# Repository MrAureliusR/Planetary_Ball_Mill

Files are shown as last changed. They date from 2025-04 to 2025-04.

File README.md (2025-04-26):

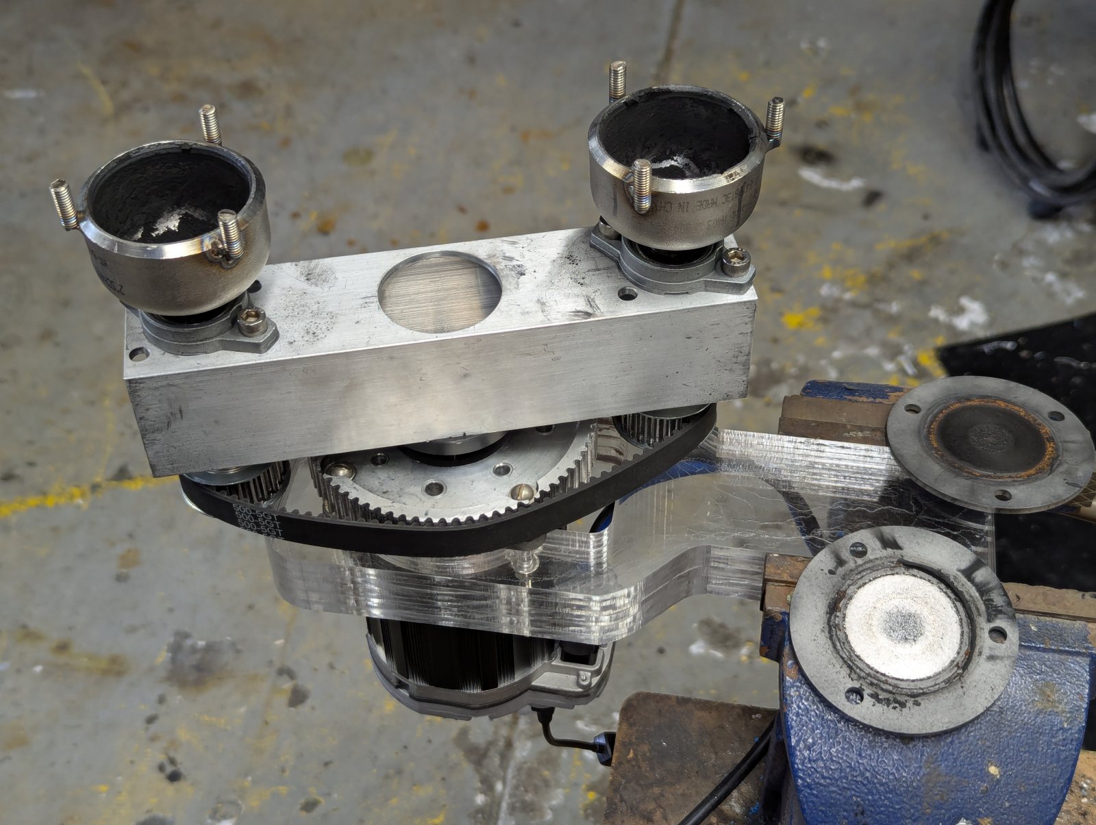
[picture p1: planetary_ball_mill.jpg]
Planetary ball mill photo Planetary Ball Mill
<br>
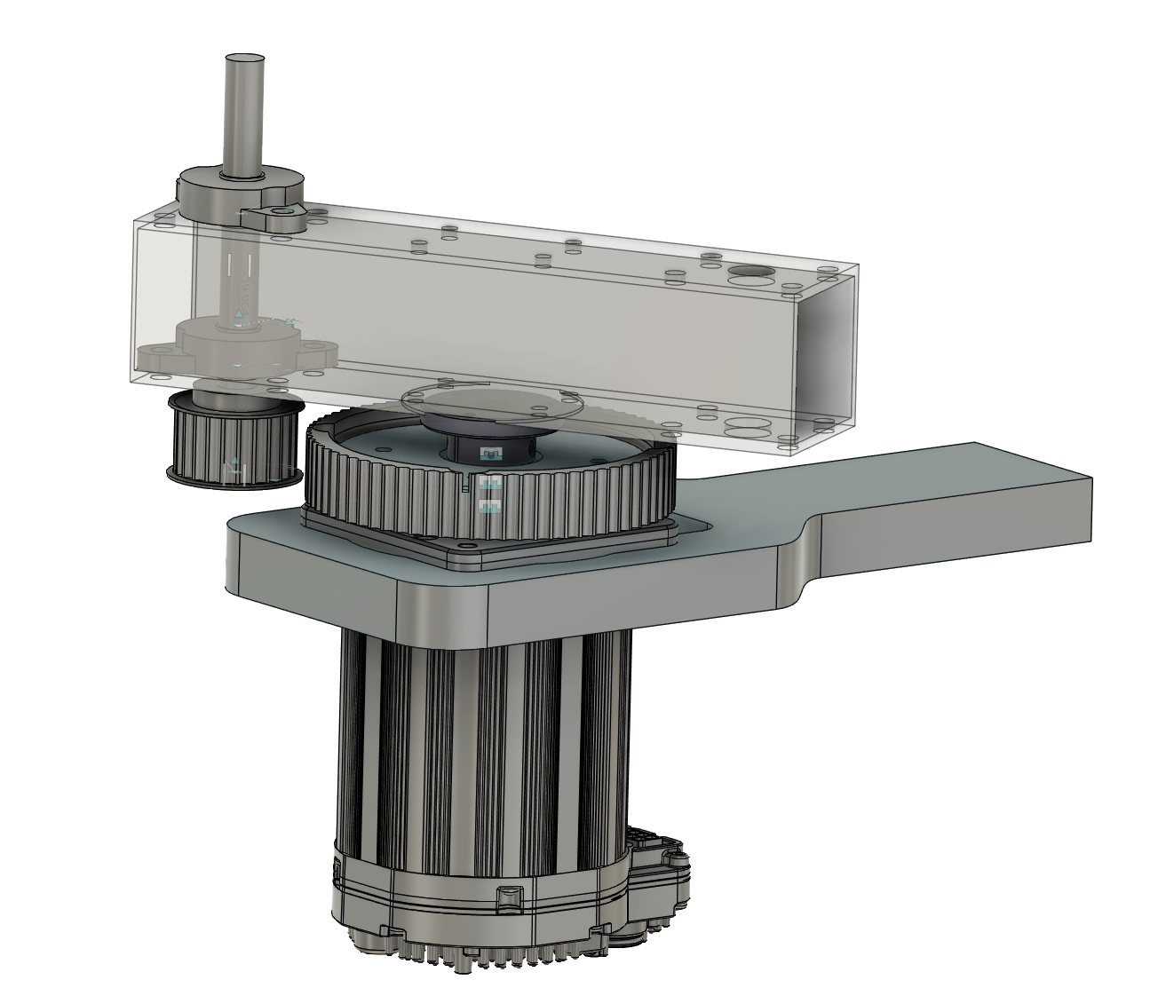
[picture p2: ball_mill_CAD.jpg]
Planetary ball mill CAD Planetary Ball Mill CAD


Modeled after this commercial device:  https://www.retsch.com/products/milling/ball-mills/planetary-ball-mill-pm-100/<br>
<br><br>
Chambers counter-rotate 2X speed of motor<br>
Chamber path radius: 85mm<br>
Chamber diameter: 50mm<br>
Chamber height: 30mm<br>
Chamber volume:  60ml (appx)<br>
<br><br>
Radius to chamber outer wall (85 + 25 =  110mm)
<br>
g-force at 600RPM:  44g
<br>
Power consumption:<br>
Idle: 16W<br>
600RPM chambers empty: 45W<br>
600RPM 15 9.5mm balls in each chamber:  110W<br>
600RPM 96 6.35mm balls in each chamber:  200W<br>
<br><br><br>

Rectangular aluminum tube (main beam):  https://www.mcmaster.com/6546K23/  $25<br>
Sun pulley:  https://phidgets.com/?prodid=779   GT5 Pulley with 17mm Bore and 72 Teeth  with hub machined away and mounting holes added  $15<br>
Planet pulley: https://phidgets.com/?prodid=770 GT5 Pulley with 12mm Bore and 24 Teeth  2x $4<br>
Belt:  https://phidgets.com/?prodid=826  500mm GT5x15mm Timing Belt  $4<br>
Flanged bearing for planet shafts: https://phidgets.com/?prodid=876  Flanged Rotary Bearing for 12mm Shaft  4x $4<br>
Keyed 12mm shaft: https://phidgets.com/?prodid=731  12mm Precision Ground Rotary Shaft (w/ keyway)   2 x 10cm  $20<br>
1/2" shaft flange:  https://motionconstrained.com/store/shaft-collars/flange-mount-shaft-collar/   $25<br>
Grinding chambers:  2" stainless steel pipe cap (welded to 12mm shaft)  https://www.mcmaster.com/45605K586/   2x $33<br>
Clearpath motor 1/2" shaft,  peak torque 13Nm, max speed 840RPM, 250W continuous: https://teknic.com/model-info/CPM-MCVC-3441S-RLN/   $388<br>
Clearpath power supply:  https://teknic.com/products/servo-motor-dc-power-supply/  $250<br>
Lids for grinding chambers:  https://sendcutsend.com/  $30<br>
Mount for motor:  Laser-cut acrylic laminated into 30mm thick stack  $10<br>
<br><br>
Total parts cost:  $832<br>
<br><br>

Hardened stainless steel grinding balls:  https://www.mcmaster.com/9529K19/  $18<br>

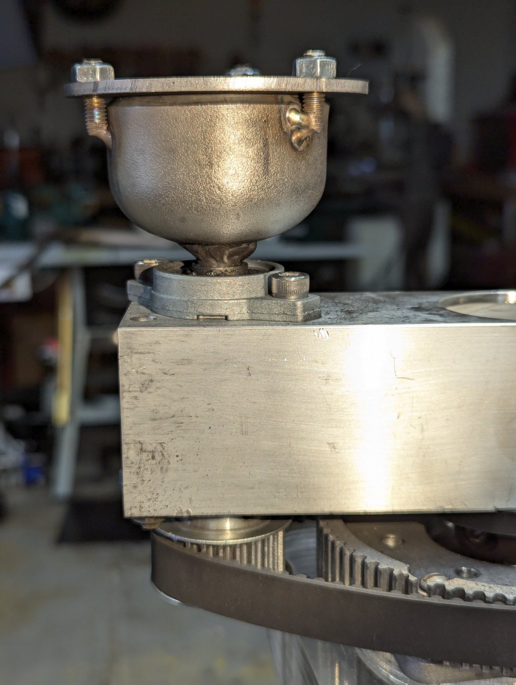
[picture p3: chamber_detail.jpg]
Planetary ball mill chamber detail Chamber welded to support shaft


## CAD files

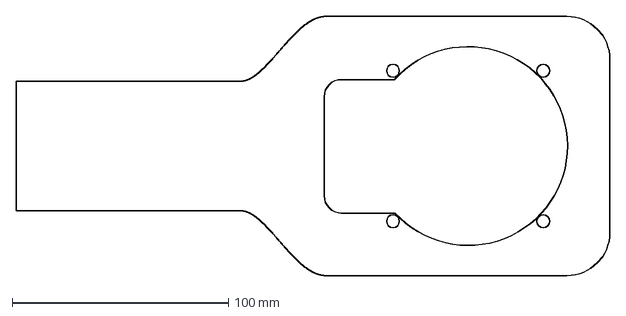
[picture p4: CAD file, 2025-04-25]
Motor_mount_Clearpath_3441.dxf
274.8 x 120.0 mm

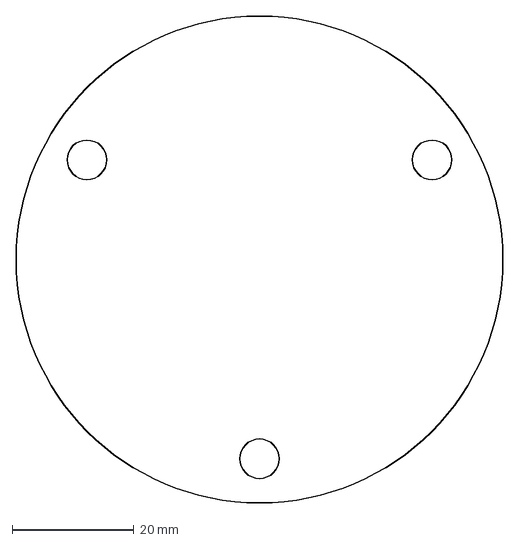
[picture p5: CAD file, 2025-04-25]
ball mill lid.dxf
80.0 x 80.0 mm
